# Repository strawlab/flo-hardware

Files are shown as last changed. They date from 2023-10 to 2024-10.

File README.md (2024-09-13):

# Fast-Lock-On (FLO) hardware



**ℹ️ The main FLO repository is at https://github.com/strawlab/flo ℹ️**.

This repository hosts build instructions and manual for the FLO Bring Your Own
(BYO) camera insect tracking/filming. Included are hardware design files and other large,
binary files.

FLO is a method for videography using a camera system that automatically moves
to follow the subject.

FLO is described in the following publication:

[FLO paper]: https://doi.org/10.1101/2023.12.20.572558

Vo-Doan TT, Titov VV, Harrap MJM, Lochner S, Straw AD. High Resolution Outdoor Videography of Insects Using Fast Lock-On Tracking. bioRxiv (2023) [doi:10.1101/2023.12.20.572558][FLO paper].

flo video rollup

## What is in this repository

### Mini-FLO

A bare-minimum hardware

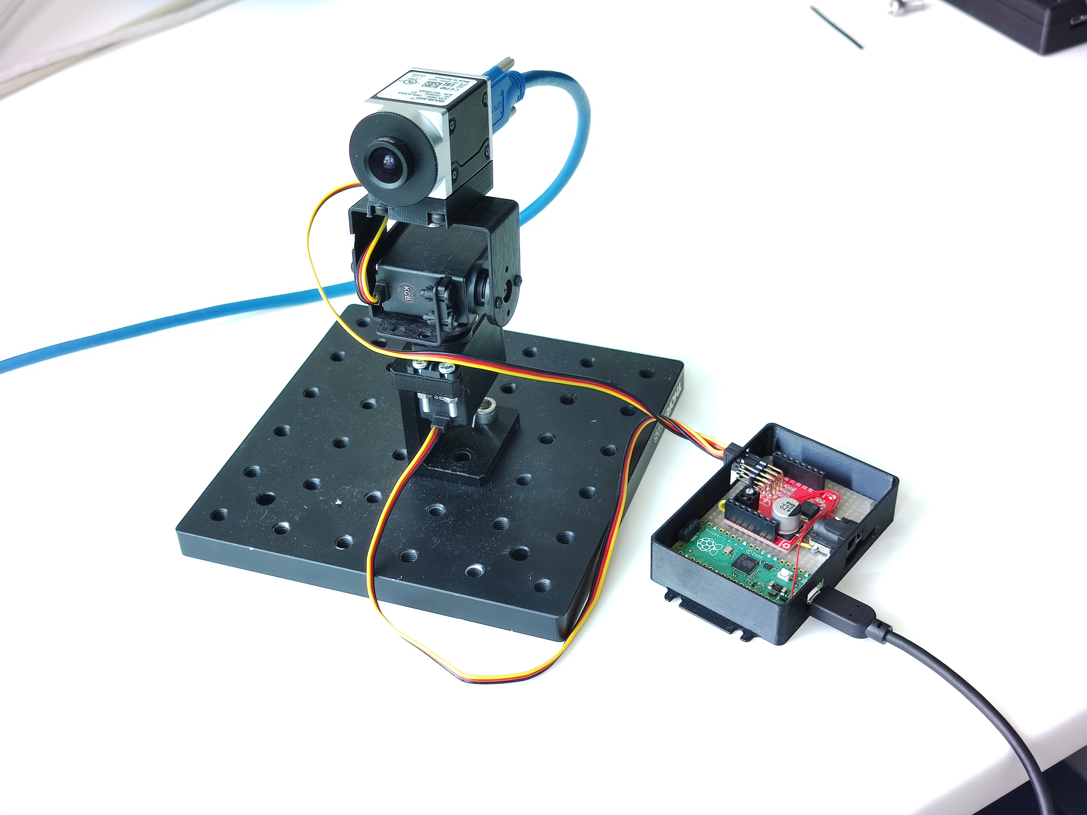
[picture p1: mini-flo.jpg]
Mini-FLO photo


### BYO-camera setup

"Bring Your Own Camera".

The setup for filming flying bees carrying a retroreflective marker.

[hardware description is in ./byo directory](./byo/readme.md)

BYO-camera setup photo

## Other links

- https://github.com/strawlab/red-button-trigger-timestamp hardware to record
  times of external trigger events.

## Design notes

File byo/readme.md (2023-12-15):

# Bill of materials

see [bom.xlsx](./bom.xlsx)

PCB files are made in KiCAD 7.0.

Some 3d-printing models were done in FreeCAD 0.21.0.32457 (pre-release of v0.21); Lattice2 and Part-o-magic community add-ons are required for editing the FreeCAD models. 

Other 3d-printing models were done in Autodesk Inventor.

The 3d models of parts are also provided in STEP and STL formats; gcode files are sliced for Prusa i3 MK3 3d printer with 0.4mm nozzle.

# System description

## overall design

## tracking cameras and illumination system

The `beam-driver` board sends trigger pulses to the two tracking cameras. The cameras send back an ExposureActive signal, which are ORed together, passed through the microcontroller (to limit the max pulse width to protect the leds and the driver from misconfiguration of exposure times) to drive the 850 nm LED beam source. Image data is sent to the PC via usb3.

Nominal exposure time is 50 microseconds, the default framerate is 150 Hz.

### beam-driver board

### beam source

These rings were designed for a different setup, and don't quite fit on the cameras of the BYO setup because they are too close to each other. So we've cut these boards, and also left some LEDs unpopulated. There is a pcb layout for the cut-down version, see `/led-ring-v2/led-ring-v2-cut`. The photo below shows the manually-cut variant of the full ring.

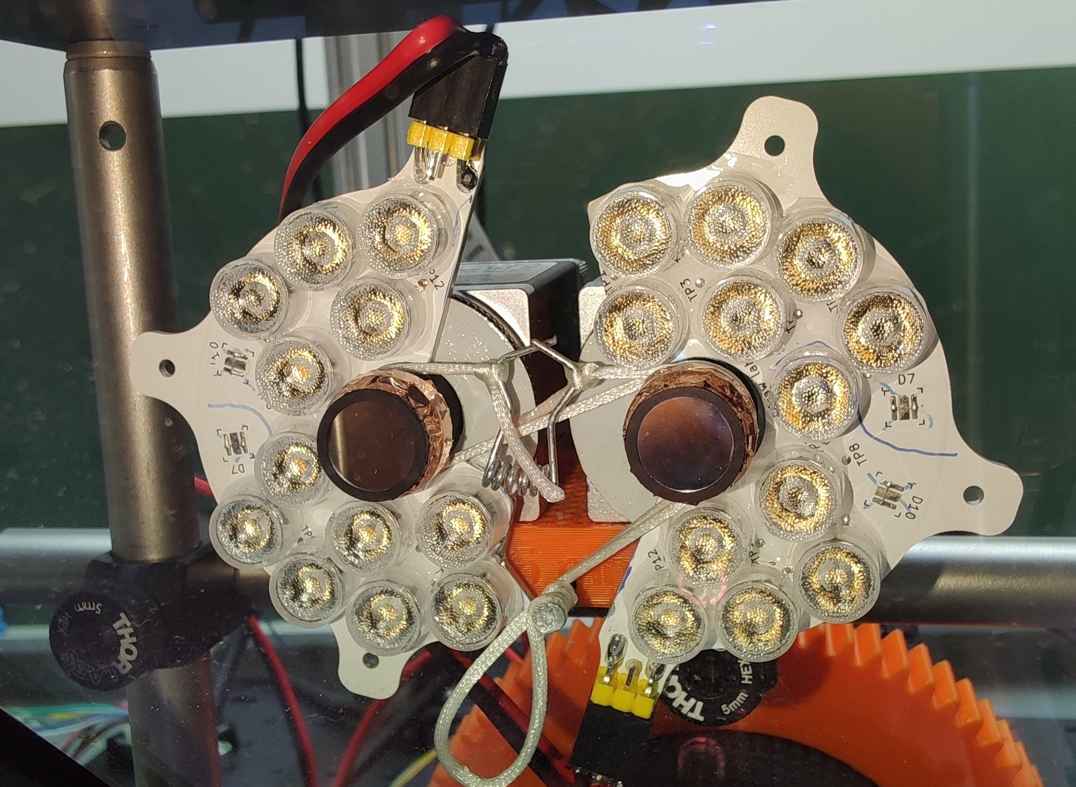
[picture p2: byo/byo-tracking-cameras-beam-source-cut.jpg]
cut beam source on byo system


### trigger cable

see [trigger cable assembly instruction](../trigger-cable/trigger-cable.md)

### tuning led current

Supply voltage directly affects the peak current of the beam source LEDs. The range allowed by the board itself is 9 to 35 V, but the actual range must be determined experimentally for each LED source. 

For our beam source (2 boards of 6-series-2-parallel SFH4715AS LEDs), the maximum supply voltage is 24 V.

1) determine the maximum current for your beam source. For example, our board uses SFH4715AS, which has a peak current rating of 3 A. We have a total of 4 string in parallel (2 strings per led board and 2 led boards), so the total current to be seen by the driver is 4 * 3 = 12 A.

2) connect one camera to the beam-driver board. Configure it for 50 us exposure. (signal generator can be used instead of a camera)

3) power the board from an adjustable power supply set to 9 V, and verify (with an oscilloscope) that you see 50-microsecond-wide pulses on the gate of the mosfet.

4) connect an oscilloscope to the SMA connector on the board with a coax cable, and set the probe division ratio to 20x (because the sense resistor is 0.05 Ohms), and the unit to Amps. (do not use 50-ohm termination on the scope).

5) crank up the supply voltage until the current pulse amplitude reaches the wanted value (12 A). Write down the voltage.

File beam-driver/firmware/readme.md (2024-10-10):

# Firmware binary

This file can be flashed onto the Raspberry Pi Pico onboard the Dual Cam PCB.
Hold the boot button while plugging in the Raspberry Pi Pico to your PC. This
will bring it up as a USB Mass Storage device onto which you can drag and drop
the `.uf2` file here.

### beamdriver-150Hz.uf2

Source code: [repo "flo", commit c64758fc95ba7cb73e0c1d8a02bef2db8ca351d4 "Merge branch 'firmware-beamdriver'"](https://github.com/strawlab/flo/tree/c64758fc95ba7cb73e0c1d8a02bef2db8ca351d4/firmware/beamdriver)

Characteristics:

- 150 fps
- lowest latency and jitter (~0.5us)
- no helpful led indication

### beamdriver-100Hz.uf2

Same source as above, compiled with `FRAMERATE` set to 100.0.

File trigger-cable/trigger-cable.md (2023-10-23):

# Trigger cable

The trigger cable connects `led-driver` board to a tracking camera. 
Two cables are needed for two cameras.

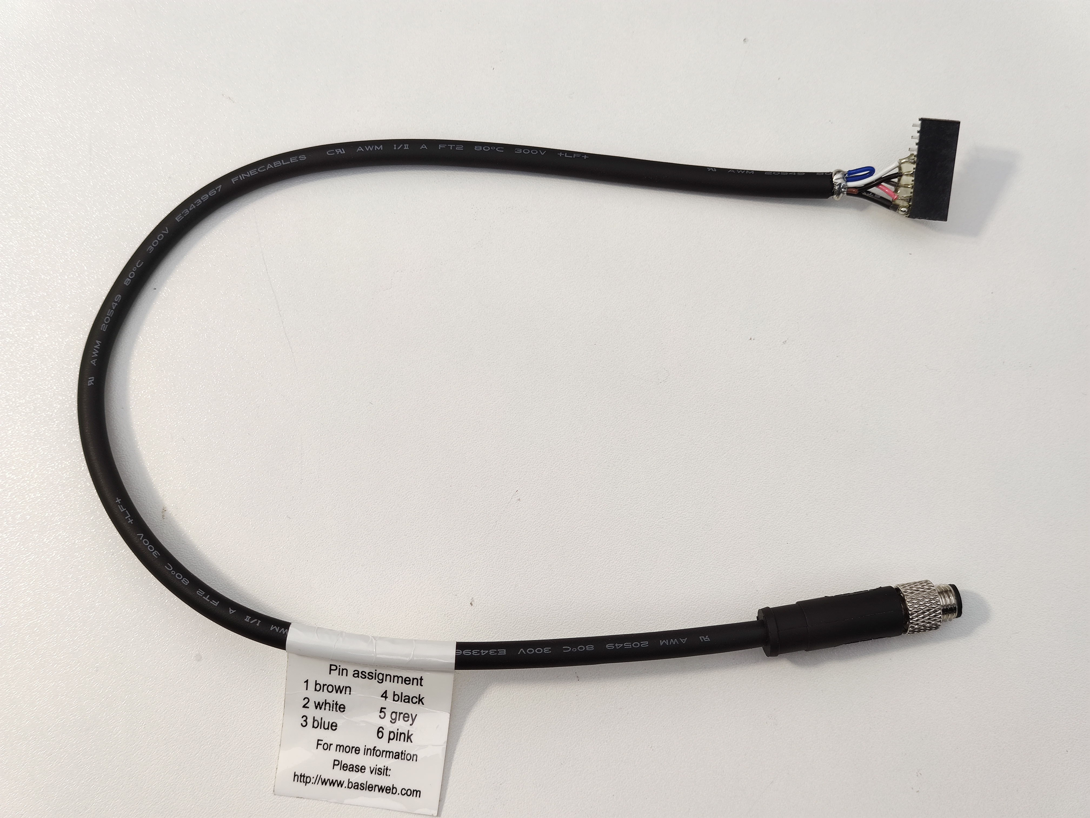
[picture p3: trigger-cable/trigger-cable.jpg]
trigger cable photo




## BOM

* Basler 2200000315
* 8x1-pin 0.1-inch socket

## Pinout

| camera connector pin  | wire color | signal        | pcb connector pin |
|-----------------------|------------|----------     |-------------------|
| 1 (nc)                | brown      | none          | none              |
| 2 (Line1)             | white      | not used      | 4                 | 
| 3 (Line1 return)      | blue       | ground        | 7, 8              | 
| 4 (Line2)             | black      | <-- trigger   | 5                 | 
| 5 (Line3)             | grey       | exposure -->  | 6                 | 
| 6 (gpio ground)       | pink       | ground        | 7, 8              | 
| shield (camera case)  |            | ground        | 7, 8              | 
|                       |            | (connector key) | 1 (plug / missing pin)              |

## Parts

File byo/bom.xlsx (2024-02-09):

no | system | type | component | brand | part number | count | detail | link | 3d model | pcb project | name on pcb
 | byo | device | high-speed camera | Mikrotron | MotionBlitz EoSens mini1 | 1
 | byo | mechanical | lens mount adapter |  | ?? | 1 | C mount to Fmount adapter
 | byo | mechanical | mounting base | Thorlabs | BA1S/M | 1 | pretty camera mount
 | byo | mechanical | cap screw 1/4''-20 3/8'' |  |  | 1 | mount ball head to post
 | byo | mechanical | ball head | Giottos | MH1004 | 1 | pretty camera mount
 | byo | optics | lens for high-speed camera | Nikon | AF Micro Nikkor 200mm f/4D | 1
 | byo/focusing | 3d-print | pinion gear |  |  | 1 | mounted onto the focusing stepper |  | byo/focusing/36jx30k5.18-pinion.FCStd
 | byo/focusing | 3d-print | motor mount |  |  | 1 |  |  | byo/focusing/36jx30k5.18-mount.FCStd
 | byo/focusing | 3d-print | ring gear |  |  | 1 | press-fit onto the barrel of the lens |  | byo/focusing/ring_gear.stl
 | byo/focusing | device | stepper driver | Trinamic | TMCM-1141 | 1
 | byo/focusing | device | power supply |  |  | 1 | 24V 1.25A
 | byo/focusing | mechanical | 1/4"-20 cap srew |  |  | 1 | fix motor mount to the lens
 | byo/focusing | mechanical | geared stepper motor | Phidgets | Phidgets id:3345_0 | 1 | NEMA17 1.8 Degree 1.68A Stepper -> 5.18:1 Gearbox, 18 kg*cm torque
 | byo/focusing | cable | USB cable |  |  | 1 | A to micro-B 3 meters, connect stepper driver to pc
 | setup | 3d-print | bottom mirror frame |  |  | 1 |  |  | byo/PanTilt/hot_mirror_holder.stl
 | setup | 3d-print | hot mirror frame |  |  | 1 |  |  | byo/PanTilt/hot_mirror_holder.stl
 | setup | laser cut | front cover |  |  | 1 |  |  | tba
 | setup | laser cut | left cover |  |  | 1 |  |  | tba
 | setup | laser cut | right corner cover |  |  | 1 |  |  | tba
 | setup | laser cut | right cover |  |  | 1 | do not cut through |  | tba
 | setup | laser cut | top right cover front |  |  | 1 |  |  | tba
 | setup | laser cut | top right cover back |  |  | 1 |  |  | tba
 | setup | laser cut | top cover |  |  | 1 |  |  | tba
 | setup | mechanical | M6x8 mm setscrew |  |  | 8 | mount all the posts to base plate
 | setup | mechanical | M4x8 mm cap screw |  |  | 4 | mount the pantilt head to the posts
 | setup | mechanical | base plate | Thorlabs | MB3060 | 1 | Aluminum Breadboard, 300 mm x 600 mm x 12.7 mm, M6 Taps
 | setup | mechanical | optical post | Thorlabs | TR250/M | 4 | 250mm D12.7
 | setup | mechanical | optical post | Thorlabs | TR200/M | 1 | 200mm D12.7
 | setup | mechanical | optical post | Thorlabs | TR150/M | 2 | 150mm D12.7
 | setup | mechanical | optical post | Thorlabs | TR20/M | 1 | 20mm D12.7
 | setup | mechanical | optical post | Thorlabs | TR30/M | 1 | 30mm D12.7
 | setup | mechanical | right-angle clamp | Thorlabs | RA90/M | 3
 | setup | mechanical | pedestal post holder | Thorlabs | BE1/M | 1
 | setup | mechanical | clamping fork | Thorlabs | CF125 | 1
 | setup | optics | bottom mirror |  |  | 1 | 1-st surface mirror, 101*127mm, 3mm thickness
 | setup | optics | hot mirror | Edmund | #64-462 | 1 | high performance hot mirror (101x127mm) that only reflects IR
 | tracking/beam | pcb | beam source |  | led-ring-v2-cut | 2 | reduced version of led-ring-v2 for byo |  |  | led-ring-v2/led-ring-v2-cut/led-ring-v2-cut.kicad_pro
 | tracking/beam/led-ring-v2-cut | 3d-print | lens carrier |  | lens holder v3 | 0 | carrier for aligning lenses onto LEDs. Only needed for assembly, not included in the final build. |  | led-ring-v2/lens holder v3.FCStd
 | tracking/beam/led-ring-v2-cut | electronic component | LED | Osram | SFH4715AS | 24 | 850 nm 2-stacked-junction high-power LED
 | tracking/beam/led-ring-v2-cut | electronic component | connector |  |  | 2 | 0.1-inch 2x6 pin header, straight
 | tracking/beam/led-ring-v2-cut | optics | lens for LED | Ledil | C17522_LISA4-M | 24 | 24-deg collimating reflector. Mounted by glueing.
 | tracking/led-driver | cable | power cable |  |  | 1 | banana to XT-30
 | tracking/led-driver | cable | led cable |  |  | 2 | approx 400 mm length 2-conductor 0.5 mm2
 | tracking/led-driver | device | adjustable power supply | Manson | HCS-3202 | 1 | adjustable power supply for led driver. Nominal 24 V 1 A. Adjusting the voltage changes led current.
 | tracking/led-driver | pcb | led driver/camera sync |  |  | 1 |  |  |  | beam-driver/dual-cam-pcb v2/dual-cam-pcb.kicad_pro
 | tracking/led-driver/dual-cam-pcb-v2 | electronic component | SMA connector through-hole | LPRS | 471-SMACONNECTOR | 1 |  |  |  | beam-driver/dual-cam-pcb v2/dual-cam-pcb.kicad_pro | J3
 | tracking/led-driver/dual-cam-pcb-v2 | electronic component | 0.1-inch socket (through-hole) 2x3 |  |  | 2 | there is a missing hole on the board as a polarity key. Plug the hole in the socket, and remove the corresponding pin from the plug. |  |  | beam-driver/dual-cam-pcb v2/dual-cam-pcb.kicad_pro | J4,J5
 | tracking/led-driver/dual-cam-pcb-v2 | electronic component | 0.1-inch pin header straight 1x3 |  |  | 2 | optional (intended for connecting pan-tilt hobby servo motors) |  |  | beam-driver/dual-cam-pcb v2/dual-cam-pcb.kicad_pro | J6, J7
 | tracking/led-driver/dual-cam-pcb-v2 | electronic component | XT-30 connector | Amass | XT30U-M | 1 |  |  |  | beam-driver/dual-cam-pcb v2/dual-cam-pcb.kicad_pro | J8
 | tracking/led-driver/dual-cam-pcb-v2 | electronic component | n-channel MOSFET | Toshiba | TK6R7P06PL | 1 |  |  |  | beam-driver/dual-cam-pcb v2/dual-cam-pcb.kicad_pro | Q1
 | tracking/led-driver/dual-cam-pcb-v2 | electronic component | resistor 20 KOhm, size 0605 |  |  | 1 |  |  |  | beam-driver/dual-cam-pcb v2/dual-cam-pcb.kicad_pro | R1
 | tracking/led-driver/dual-cam-pcb-v2 | electronic component | resistor 510 ohm, size 0605 |  |  | 1 |  |  |  | beam-driver/dual-cam-pcb v2/dual-cam-pcb.kicad_pro | R10
 | tracking/led-driver/dual-cam-pcb-v2 | electronic component | resistor 10 ohms, size 0605 |  |  | 1 |  |  |  | beam-driver/dual-cam-pcb v2/dual-cam-pcb.kicad_pro | R11
 | tracking/led-driver/dual-cam-pcb-v2 | electronic component | resistor 0.05 ohm, size 2010 | Ohmite | LVK12R050DER | 1 |  |  |  | beam-driver/dual-cam-pcb v2/dual-cam-pcb.kicad_pro | R12
 | tracking/led-driver/dual-cam-pcb-v2 | electronic component | 1 Ohm 1 W through-hole resistor | SEI Stackpole | RSMF2JT1R00 | 4 |  |  |  | beam-driver/dual-cam-pcb v2/dual-cam-pcb.kicad_pro | R14,R16,R15,R17
 | tracking/led-driver/dual-cam-pcb-v2 | electronic component | MLCC 10uF 16V, size 0805 |  |  | 1 | bypass cap, value is not critical |  |  | beam-driver/dual-cam-pcb v2/dual-cam-pcb.kicad_pro | C1
 | tracking/led-driver/dual-cam-pcb-v2 | electronic component | resistor 51 ohms, size 0605 | Yageo | RT0603DRE0751RL | 9 |  |  |  | beam-driver/dual-cam-pcb v2/dual-cam-pcb.kicad_pro | R19,R6,R2,R3,R8,R13,R5,R18,R4
 | tracking/led-driver/dual-cam-pcb-v2 | electronic component | resistor 1 KOhm, size 0605 |  |  | 2 |  |  |  | beam-driver/dual-cam-pcb v2/dual-cam-pcb.kicad_pro | R20,R21
 | tracking/led-driver/dual-cam-pcb-v2 | electronic component | resistor 10 KOhm, size 0605 |  |  | 1 |  |  |  | beam-driver/dual-cam-pcb v2/dual-cam-pcb.kicad_pro | R7
 | tracking/led-driver/dual-cam-pcb-v2 | electronic component | resistor 4.3 KOhm, size 0605 |  |  | 1 |  |  |  | beam-driver/dual-cam-pcb v2/dual-cam-pcb.kicad_pro | R9
 | tracking/led-driver/dual-cam-pcb-v2 | electronic component | Raspberry-Pi Pico | Raspberry-Pi | Raspberry-Pi Pico | 1 |  |  |  | beam-driver/dual-cam-pcb v2/dual-cam-pcb.kicad_pro | U1
 | tracking/led-driver/dual-cam-pcb-v2 | electronic component | gate driver UCC27624DR | Texas Instruments | UCC27624DR | 1 |  |  |  | beam-driver/dual-cam-pcb v2/dual-cam-pcb.kicad_pro | U2
 | tracking/led-driver/dual-cam-pcb-v2 | electronic component | LM317L (SOT-89) | Texas Instruments | LM317LIPK | 1 |  |  |  | beam-driver/dual-cam-pcb v2/dual-cam-pcb.kicad_pro | U3
 | tracking/led-driver/dual-cam-pcb-v2 | electronic component | 7805 (TO220) | JRC | NJM7805FA | 1 |  |  |  | beam-driver/dual-cam-pcb v2/dual-cam-pcb.kicad_pro | U4
 | tracking/led-driver/dual-cam-pcb-v2 | electronic component | MLCC 1uF 35V, size 0805 |  |  | 1 | bypass cap, value is not critical |  |  | beam-driver/dual-cam-pcb v2/dual-cam-pcb.kicad_pro | C2
 | tracking/led-driver/dual-cam-pcb-v2 | electronic component | Electrolytic capacitor 3300uF 35V |  |  | 1 | overkill. 1200uF should be enough. |  |  | beam-driver/dual-cam-pcb v2/dual-cam-pcb.kicad_pro | C3
 | tracking/led-driver/dual-cam-pcb-v2 | electronic component | MLCC 22uF 6.5V, size 0805 | Kyocera | CM105X5R226M16AT | 1 | affects stability of 7805, value is important |  |  | beam-driver/dual-cam-pcb v2/dual-cam-pcb.kicad_pro | C7
 | tracking/led-driver/dual-cam-pcb-v2 | electronic component | MLCC 200pF 6.5V, size 0603 |  |  | 2 | emi filter, value is important |  |  | beam-driver/dual-cam-pcb v2/dual-cam-pcb.kicad_pro | C8,C9
 | tracking/led-driver/dual-cam-pcb-v2 | electronic component | schottky diode (Micro-MELF) | Vishay | BAS85-GS08 | 2 |  |  |  | beam-driver/dual-cam-pcb v2/dual-cam-pcb.kicad_pro | D2,D1
 | tracking/led-driver/dual-cam-pcb-v2 | electronic component | schottky diode size 0805 | Kyocera | SD0805S020S1R0 | 3 |  |  |  | beam-driver/dual-cam-pcb v2/dual-cam-pcb.kicad_pro | D4,D5,D3
 | tracking/led-driver/dual-cam-pcb-v2 | electronic component | 0.1 inch pin header straight 1x8 |  |  | 2 |  |  |  | beam-driver/dual-cam-pcb v2/dual-cam-pcb.kicad_pro | J2,J1
 | tracking/led-driver/led-cable | electronic component | led-side connector |  |  | 2 | 2x6 0.1-inch socket
 | tracking/led-driver/led-cable | electronic component | driver-side connector |  |  | 2 | 2x6 0.1-inch pin header
 | tracking/led-driver/led-cable | electronic component | ferrite bead | Kemet | ESD-R-10E | 2
 | tracking/led-driver/power-cable | electronic component | power connector | Amass | XT30U | 1
 | tracking/pantilt | 3d-print | Pan motor pulley |  |  | 1 |  |  | byo/PanTilt/Pan_Pulley_17.stl
 | tracking/pantilt | 3d-print | Pan motor plate |  |  | 1 |  |  | byo/PanTilt/Pan_motor_plate.stl
 | tracking/pantilt | 3d-print | Pan motor stopper |  |  | 1 |  |  | byo/PanTilt/Pan_motor_stop.stl
 | tracking/pantilt | 3d-print | Pan rotor |  |  | 1 |  |  | byo/PanTilt/Pan_Rotor_245.stl
 | tracking/pantilt | 3d-print | Pan base |  |  | 1 |  |  | byo/PanTilt/Pan_base.stl
 | tracking/pantilt | 3d-print | Pan bearing stopper bottom |  |  | 1 |  |  | byo/PanTilt/Pan_bearing_stop_bottom.stl
 | tracking/pantilt | 3d-print | Pan bearing stopper top |  |  | 1 |  |  | byo/PanTilt/Pan_bearing_stop_top.stl
 | tracking/pantilt | 3d-print | Tilt base |  |  | 1 |  |  | byo/PanTilt/Tilt_base.stl
 | tracking/pantilt | 3d-print | Tilt motor base |  |  | 1 |  |  | byo/PanTilt/Tilt_base_motor_side.stl
 | tracking/pantilt | 3d-print | Tilt motor pulley |  |  | 1 |  |  | byo/PanTilt/Tilt_Motor_pulley_20.stl
 | tracking/pantilt | 3d-print | Tilt motor spacer |  |  | 1 |  |  | byo/PanTilt/Tilt_motor_spacer.stl
 | tracking/pantilt | 3d-print | Tilt bearing stopper |  |  | 2 |  |  | byo/PanTilt/Tilt_bearing_stop.stl
 | tracking/pantilt | 3d-print | Pantilt head cover |  |  | 1 |  |  | byo/PanTilt/Pan_cover.stl
 | tracking/pantilt | 3d-print | Pan tensioner knot |  |  | 1 |  |  | byo/PanTilt/Pan_tension_knot.stl
 | tracking/pantilt | 3d-print | Tilt bearing |  | 61802-2RS | 2 | ball bearing 61802-2RS
 | tracking/pantilt | 3d-print | Tilt rotor |  |  | 1 |  |  | byo/PanTilt/Tilt_mirror_rotor.stl
 | tracking/pantilt | 3d-print | Tilt rotor pulley |  |  | 1 |  |  | byo/PanTilt/Tilt_Rotor_pulley_100.stl
 | tracking/pantilt | 3d-print | moving mirror assembly |  |  | 1 |  |  | ??
 | tracking/pantilt | cable | USB cable |  |  | 2 | A to micro-B 3 meters, connect steppers to pc
 | tracking/pantilt | device | smart stepper | Trinamic | PD42-2-1240-TMCL | 2
 | tracking/pantilt | device | power supply |  |  | 2 | 12V 2A power supply for smart stepper
 | tracking/pantilt | electronic component | wires for smart stepper | Trinamic | TMCM-110-CABLE | 2 | 4-pin JST-PH connector with wires, for powering steppers
 | tracking/pantilt | mechanical | M5x30 cap srew |  |  | 1 | press fit to the pan tension knot and use for adjusting pan belt tesion
 | tracking/pantilt | mechanical | M3x8 cap srew |  |  | 8 | mount pan motor to pan motor plate and the tilt bases to pan rotor
 | tracking/pantilt | mechanical | M3x12 cap screw |  |  | 4 | mount tilt motor to tilt motor base
 | tracking/pantilt | mechanical | M1.5x5 cap srew |  |  | 8 | fixed pan bearing stoper top to pan base
 | tracking/pantilt | mechanical | M5 female insert |  |  | 1 | heat by soldering iron and insert to the pan motor plate
 | tracking/pantilt | mechanical | M3 female insert |  |  | 4 | heat by soldering iron and insert to the pan rotor
 | tracking/pantilt | mechanical | belt (pan) |  | 256MXL | 1 | GT2 profile 256 teeth 6.5mm width
 | tracking/pantilt | mechanical | belt (tilt) |  | 880MXL | 1 | GT2 profile 110 teeth 5mm width
 | tracking/pantilt | optics | mirror |  |  | 1 | 1-st surface mirror, 140*140mm square with 16mm chamfer on corners, thickness 3mm
 | tracking/pantilt/panbearing | 3d-print | Pan bearing inner cage |  |  | 1 |  |  | byo/PanTilt/Pan_bearing_inner.stl
 | tracking/pantilt/panbearing | 3d-print | Pan bearing middle ring |  |  | 1 |  |  | byo/PanTilt/Pan_bearing_middle.stl
 | tracking/pantilt/panbearing | 3d-print | Pan bearing outer cage |  |  | 1 |  |  | byo/PanTilt/Pan_bearing_outter.stl
 | tracking/pantilt/panbearing | mechanical | Pan bearing balls (4.5 mm) |  |  | 12 | 4.5 mm stainless steal ball insert to the pan bearing
 | tracking/sensor | 3d-print | camera mount |  |  | 1 |  |  | byo/2cam-plate-35mm/2cam-plate-35mm.FCStd
 | tracking/sensor/camera | cable | USB cable |  |  | 2 | USB3 cable for connecting the camera to the PC
 | tracking/sensor/camera | cable | trigger cable | Basler | 2200000315 | 2
 | tracking/sensor/camera | device | tracking camera | Basler | a2A 1920 - 160umBAS | 2 | monochrome, ir-sensitive camera. The front of the case must be machined to make it CS-mount.
 | tracking/sensor/camera | mechanical | CS to S-mount lens adapter | Basler | 2000035953 | 2
 | tracking/sensor/camera | optics | lens | IDS-imaging | IDS-5M12-S2524F | 2 | 25-mm, 1/2in sensor, S-mount (has ir-blocking filter which must be removed)
 | tracking/sensor/camera | optics | IR bandpass filter | Thorlabs | FBH05850-10 | 2 | 850 nm, fwhm=10 nm
 |  |  | PC |  |  | 1 | amd ryzen 9 3900x, 32G ram, nvidia rtx3060ti

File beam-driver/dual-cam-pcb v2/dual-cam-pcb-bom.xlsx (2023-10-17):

Id | Designator | Footprint | Quantity | Designation | Supplier and ref | brand | comment
23 | C1 | C_0805_2012Metric_Pad1.18x1.45mm_HandSolder | 1 | MLCC 10uF 16V, size 0805 |  |  | bypass cap, value is not critical
26 | C2 | C_0805_2012Metric_Pad1.18x1.45mm_HandSolder | 1 | MLCC 1uF 35V, size 0805 |  |  | bypass cap, value is not critical
8 | C3 | CP_Radial_D18.0mm_P7.50mm | 1 | Electrolytic capacitor 3300uF 35V |  |  | overkill. 1200uF should be enough.
17 | C7 | C_0805_2012Metric_Pad1.18x1.45mm_HandSolder | 1 | MLCC 22uF 6.5V, size 0805 |  |  | affects stability of 7805, value is important
25 | C8,C9 | C_0603_1608Metric_Pad1.08x0.95mm_HandSolder | 2 | MLCC 200pF 6.5V, size 0603 |  |  | emi filter, value is important
21 | D2,D1 | D_MicroMELF_Handsoldering | 2 | schottky diode (Micro-MELF) | BAS85-GS08 | Vishay
12 | D4,D5,D3 | D_0805_2012Metric_Pad1.15x1.40mm_HandSolder | 3 | schottky diode size 0805 | SD0805S020S1R0 | Kyocera
3 | J2,J1 | PinHeader_1x08_P2.54mm_Vertical | 2 | 0.1 inch pin header straight 1x8
2 | J3 | SMA_Amphenol_901-144_Vertical | 1 | SMA connector through-hole | 471-SMACONNECTOR | LPRS
4 | J4,J5 | Conn_LED_source | 2 | 0.1-inch socket (through-hole) 2x3 |  |  | there is a missing hole on the board as a polarity key. Plug the hole in the socket, and remove the corresponding pin from the plug.
9 | J6, J7 | PinHeader_1x03_P2.54mm_Vertical | 2 | 0.1-inch pin header straight 1x3 |  |  | optional (intended for connecting pan-tilt hobby servo motors)
7 | J8 | AMASS_XT30U-M_1x02_P5.0mm_Vertical | 1 | XT-30 connector | XT60U-M | Amass
22 | Q1 | TO-252-2 | 1 | n-channel MOSFET | TK6R7P06PL | Toshiba
24 | R1 | R_0603_1608Metric_Pad0.98x0.95mm_HandSolder | 1 | resistor 20 KOhm, size 0605
19 | R10 | R_0603_1608Metric_Pad0.98x0.95mm_HandSolder | 1 | resistor 510 ohm, size 0605
11 | R11 | R_0603_1608Metric_Pad0.98x0.95mm_HandSolder | 1 | resistor 10 ohms, size 0605
14 | R12 | R_2010_5025Metric_Pad1.40x2.65mm_HandSolder | 1 | resistor 0.05 ohm, size 2010 | LVK12R050DER | Ohmite
1 | R14,R16,R15,R17 | R_Axial_DIN0411_L9.9mm_D3.6mm_P5.08mm_Vertical | 4 | 1 Ohm 1 W through-hole resistor
13 | R19,R6,R2,R3,R8,R13,R5,R18,R4 | R_0603_1608Metric_Pad0.98x0.95mm_HandSolder | 9 | resistor 51 ohms, size 0605
18 | R20,R21 | R_0603_1608Metric_Pad0.98x0.95mm_HandSolder | 2 | resistor 1 KOhm, size 0605
16 | R7 | R_0603_1608Metric_Pad0.98x0.95mm_HandSolder | 1 | resistor 10 KOhm, size 0605
27 | R9 | R_0603_1608Metric_Pad0.98x0.95mm_HandSolder | 1 | resistor 4.3 KOhm, size 0605
5 | U1 | RPi_Pico_SMD | 1 | Raspberry-Pi Pico | Raspberry-Pi Pico | Raspberry-Pi
20 | U2 | SOIC-8_3.9x4.9mm_P1.27mm | 1 | gate driver UCC27624DR | UCC27624DR | Texas Instruments
15 | U3 | SOT-89-3 | 1 | LM317L (SOT-89) | LM317LIPK | Texas Instruments
6 | U4 | TO-220-3_Vertical | 1 | 7805 (TO220) | NJM7805FA | JRC

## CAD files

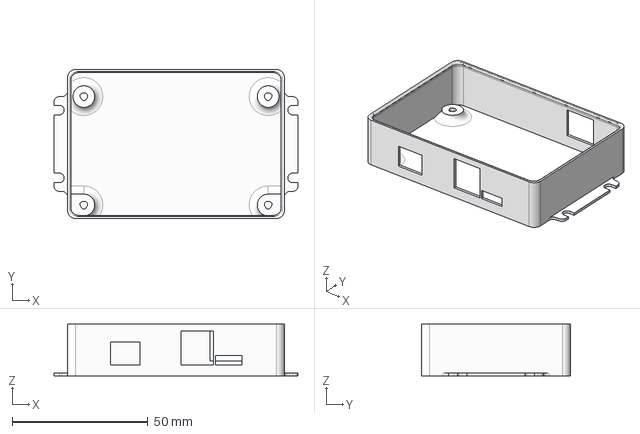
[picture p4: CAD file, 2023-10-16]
beam-driver/board outline.FCStd
90.0 x 55.0 x 19.0 mm

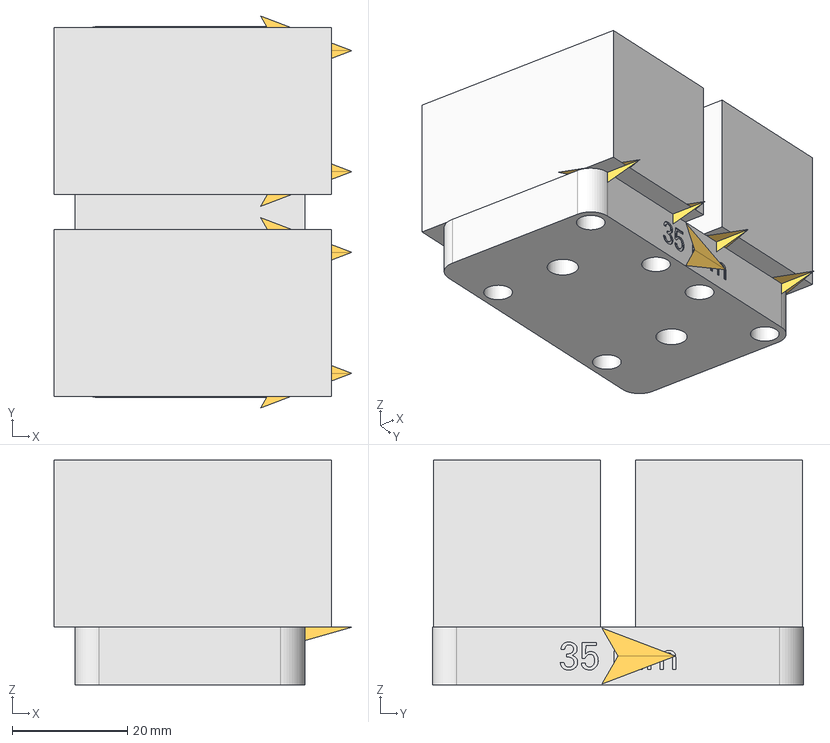
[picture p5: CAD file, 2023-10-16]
byo/2cam-plate-35mm/2cam-plate-35mm.FCStd
51.7 x 68.0 x 39.0 mm
BoundBox of ace2_a2a_ultra_simplified
BoundBox of ace2_a2a_ultra_simplified001
PlacementSubsequence
Placment002
Placment003

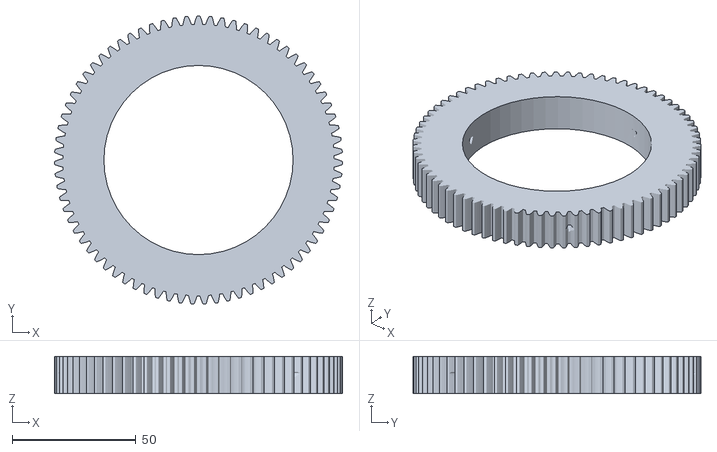
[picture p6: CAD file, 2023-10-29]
byo/focusing/ring_gear.stl
116.5 x 116.5 x 15.0

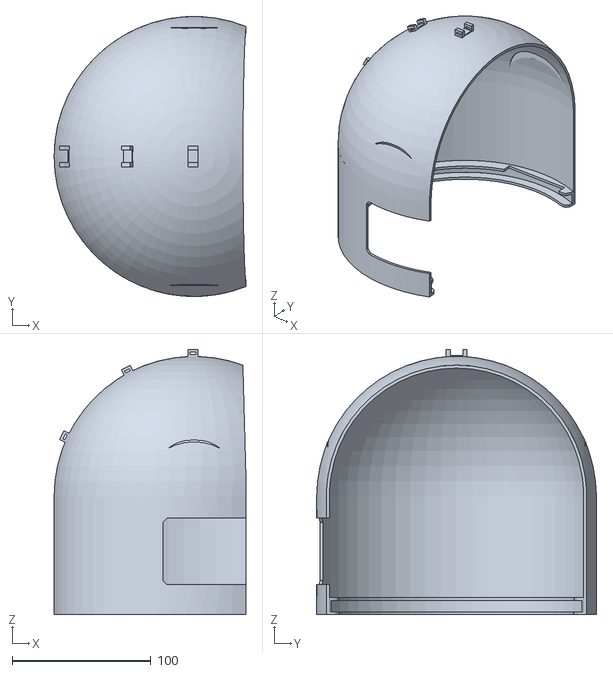
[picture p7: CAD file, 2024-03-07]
byo/PanTilt/Pan_cover_2mm.stl
138.3 x 201.9 x 191.2

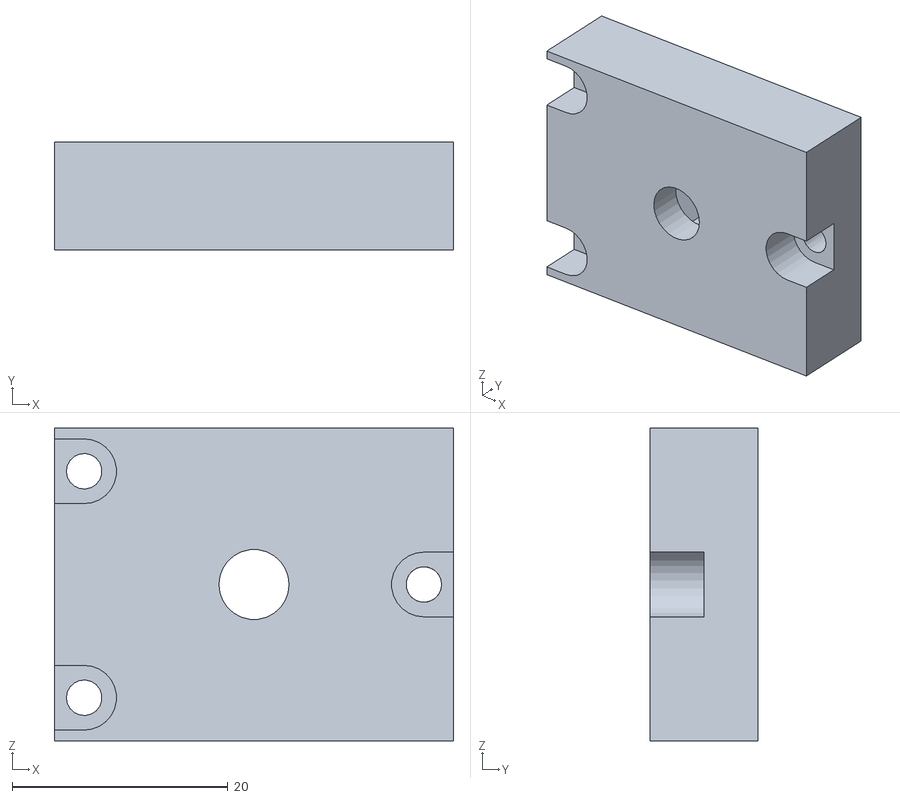
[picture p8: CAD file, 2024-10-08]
mini-pan-tilt/a2A1920_adapter_6mm.stl
37.0 x 10.0 x 29.0

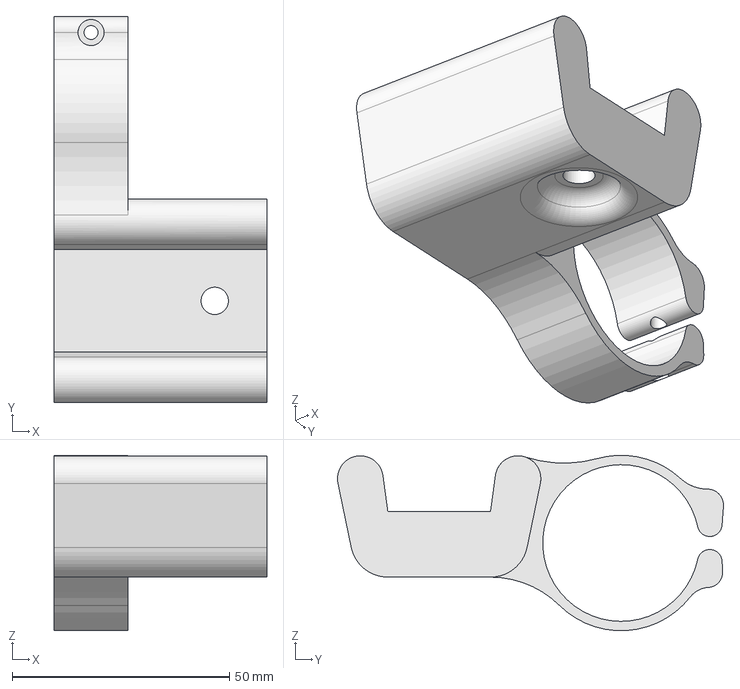
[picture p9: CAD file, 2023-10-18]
byo/focusing/36jx30k5.18-mount.step
49.0 x 88.9 x 40.4 mm

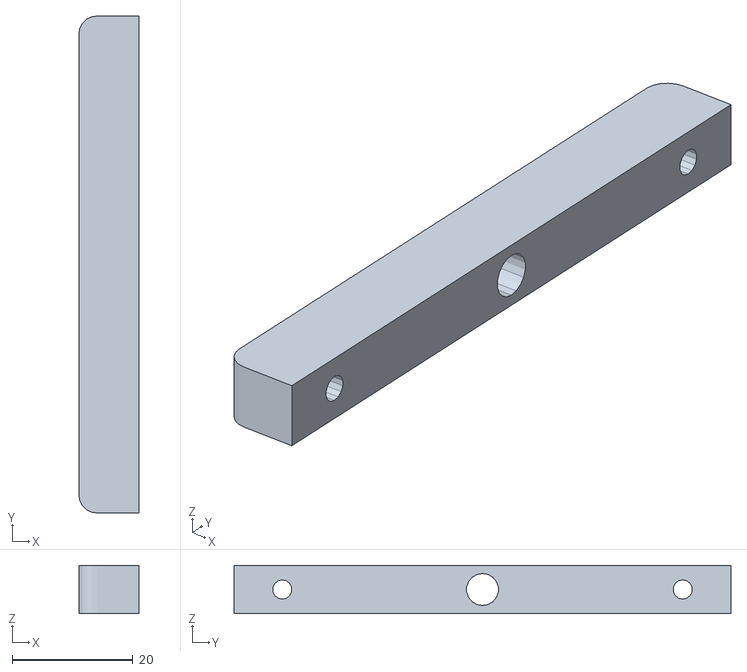
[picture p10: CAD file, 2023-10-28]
byo/PanTilt/Pan_motor_stop.stl
10.0 x 82.3 x 8.00

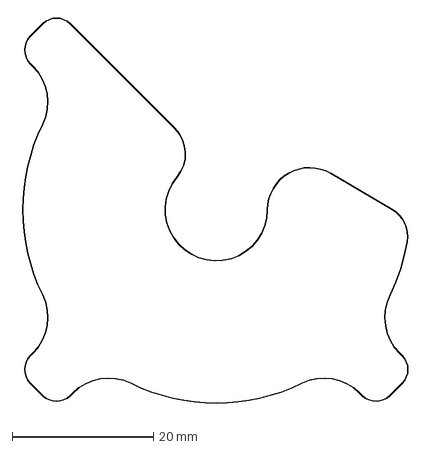
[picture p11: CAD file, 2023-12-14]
led-ring-v2/10mm lens packing (cut version)-board outline.dxf
55.8 x 55.8 mm

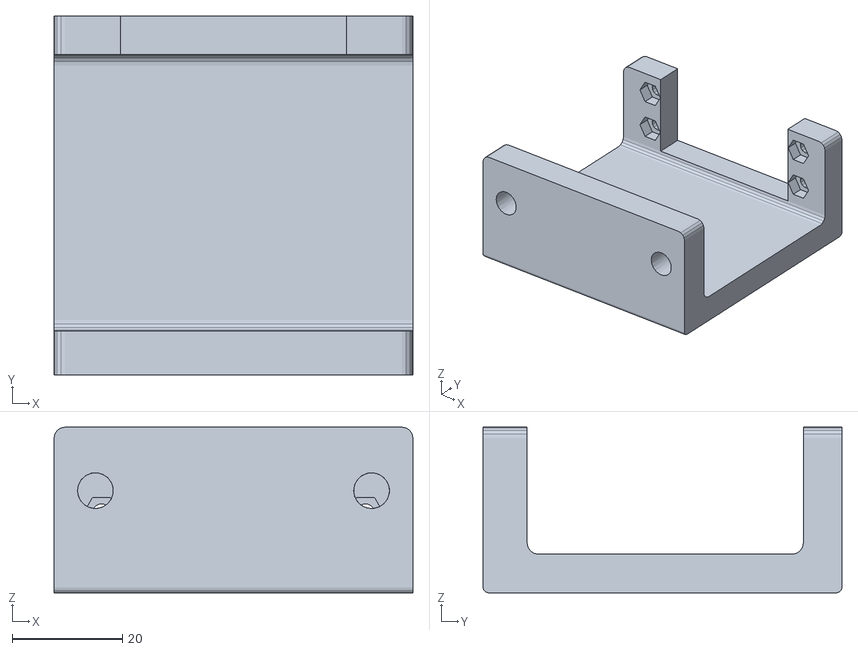
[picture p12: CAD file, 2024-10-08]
mini-pan-tilt/motor_holder.stl
65.0 x 65.0 x 30.0

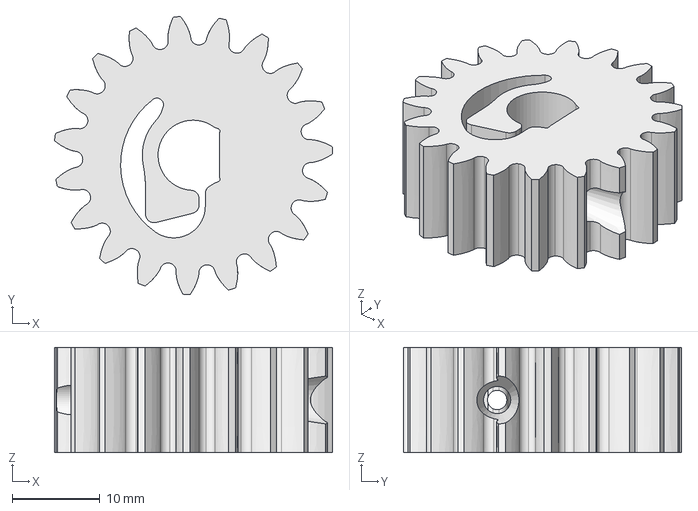
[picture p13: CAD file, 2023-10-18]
byo/focusing/36jx30k5.18-pinion.step
31.7 x 31.7 x 12.0 mm

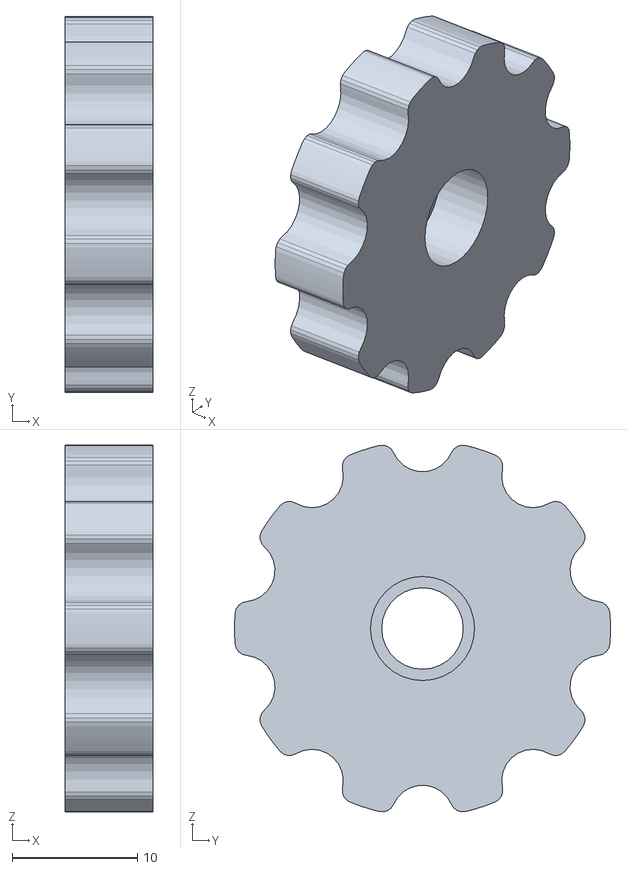
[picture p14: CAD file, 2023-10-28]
byo/PanTilt/Pan_tension_knot.stl
7.00 x 30.0 x 29.2

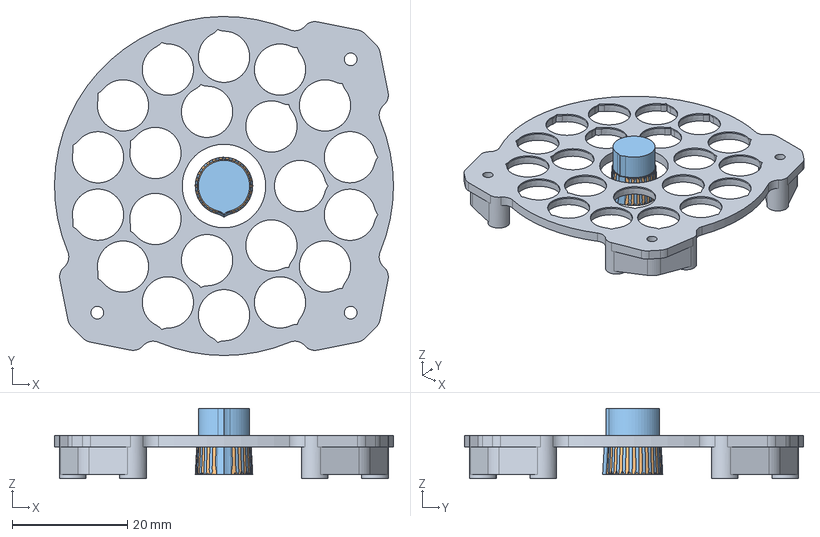
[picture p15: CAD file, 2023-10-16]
led-ring-v2/lens holder v2.FCStd
58.9 x 58.9 x 12.2 mm
lens holder
lens shape
cavity cutter

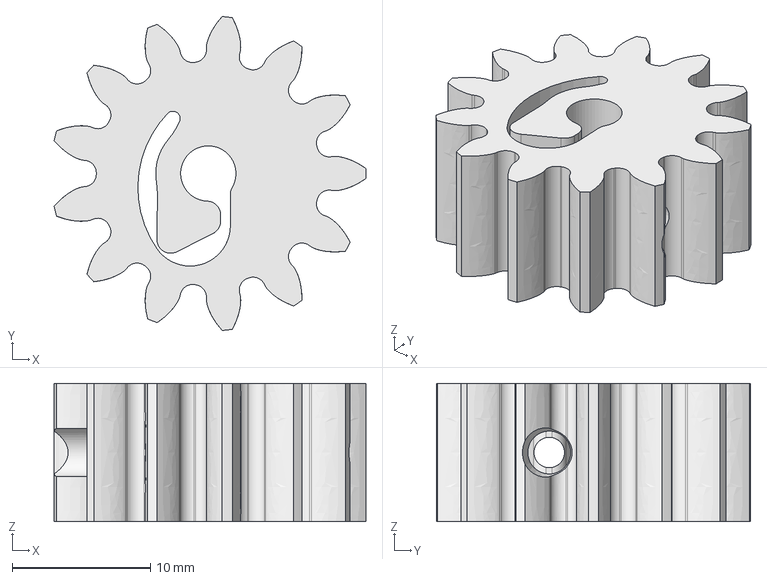
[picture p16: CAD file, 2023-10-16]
byo/focusing/nema08-pinion.FCStd
22.6 x 22.7 x 10.0 mm

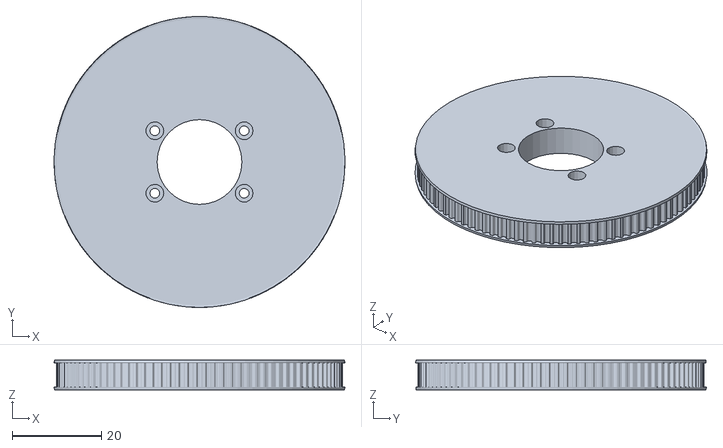
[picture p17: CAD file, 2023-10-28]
byo/PanTilt/Tilt_Rotor_pulley_100.stl
65.2 x 65.2 x 6.65

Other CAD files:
led-ring-v2/10mm lens packing (cut version).FCStd
led-ring-v2/pasting plate.FCStd
byo/PanTilt/Pan_cover.stl
led-ring-v2/10mm lens packing-Compound.dxf
byo/2cam-plate-35mm/2cam-plate-35mm.stl
byo/PanTilt/Pan_Pulley_17.stl
byo/PanTilt/Pan_Rotor_245.stl
byo/PanTilt/Pan_base.stl
byo/PanTilt/Pan_bearing_inner.stl
byo/PanTilt/Pan_bearing_middle.stl
byo/PanTilt/Pan_bearing_outter.stl
byo/PanTilt/Pan_bearing_stop_bottom.stl
byo/PanTilt/Pan_bearing_stop_top.stl
byo/PanTilt/Pan_motor_plate.stl
byo/PanTilt/Tilt_Motor_pulley_20.stl
byo/PanTilt/Tilt_base.stl
byo/PanTilt/Tilt_base_motor_side.stl
byo/PanTilt/Tilt_bearing_stop.stl
byo/PanTilt/Tilt_mirror_rotor.stl
byo/PanTilt/Tilt_motor_spacer.stl
byo/PanTilt/hot_mirror_holder.stl
byo/focusing/36jx30k5.18-mount.FCStd
byo/focusing/36jx30k5.18-mount.stl
byo/focusing/36jx30k5.18-pinion.FCStd
byo/focusing/36jx30k5.18-pinion.stl
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

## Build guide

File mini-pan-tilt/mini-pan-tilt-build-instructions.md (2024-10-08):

# Build instructions and user manual for the proof-of-concept Mini-Pan-Tilt (MPT) version of the Fast-Lock-On (FLO) insect tracking system

This manual is a step-by-step guide to assemble a mini-pan-tilt setup from
scratch and run it on an Ubuntu Linux machine.

## Bill of Materials

All parts but one, the custom 3D-printed support bracket _(CAD file included)_ are available as off-the-shelf components.

### Mechanical parts

- 1x Lynxmotion: Lynx B - Pand and Tilt Kit (Black Anodized), inluding:

  - 1x Aluminum Multi-Purpose Servo Bracket Single (ASB-04)
  - 1x Auminum "C" Servo Bracket Single (ASB-03)
  - 2x HS-422 standard servo (S422)
  - Hardware (in particular: 4x small black screws for servos, 1x black M1 screw with washer and nut for tilt axis, nylon rivets)

  There seems to be the newer version of this kit, available [here](https://www.robotshop.com/products/lynxmotion-pan-and-tilt-kit-aluminium2).

- 1x [Thorlabs base plate 150x150x12.7 mm, M6 Taps](https://www.thorlabs.de/thorproduct.cfm?partnumber=MB1515/M) +

- 1x [custom 3D printed support bracket](motor_holder.stl)

- 1x Basler Tripod Adapter, compatible with camera (see [below](#optical), e.g. [this one](https://www.edmundoptics.eu/p/ace2-14-tripod-mount-adapter/44087/)). Alternatively, there is also a 3D [printed version](a2A1920_adapter_6mm.stl) of this part.
  )
- assorted screws

  - 4x M3x20 cap screws + nuts

  - 1x M6 cap screw

  - screws required for the camera adapter

### Electronics

- [Raspberry Pi Pico](https://www.raspberrypi.com/products/raspberry-pi-pico/) microcontroller
- optional: breadboard jumper wires

### Optical

- Basler or Vimba high-framerate, USB 3.0 camera: highly recommended [Basler Ace2 a2a1920-160mBAS](https://www.baslerweb.com/en/shop/a2a1920-160umbas/)
- CS-mount lens of desired specifications. Recommended for this basic setup: f=16mm A=1:1.6
- optional: IR-bandpass filter for better signal-to-noise ratio

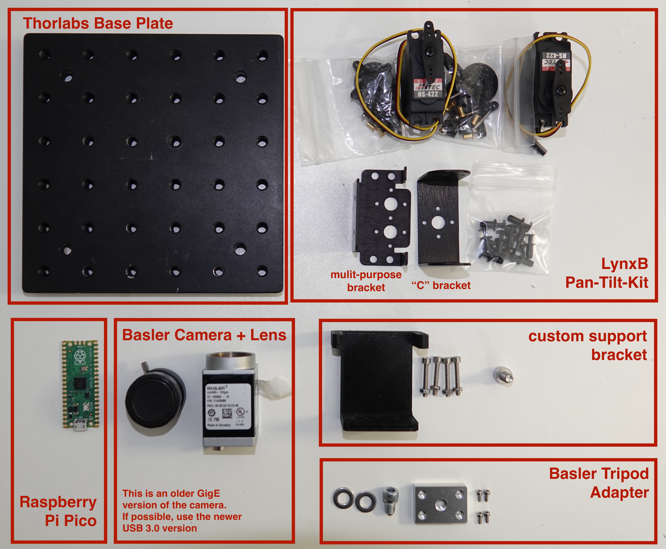
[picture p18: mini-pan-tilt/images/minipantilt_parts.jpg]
parts


## Hardware build instruction

1. Mount camera on "C" bracket :
   - Attach tripod adapter to base of camera
   - Attach "C" Bracket to Adapter

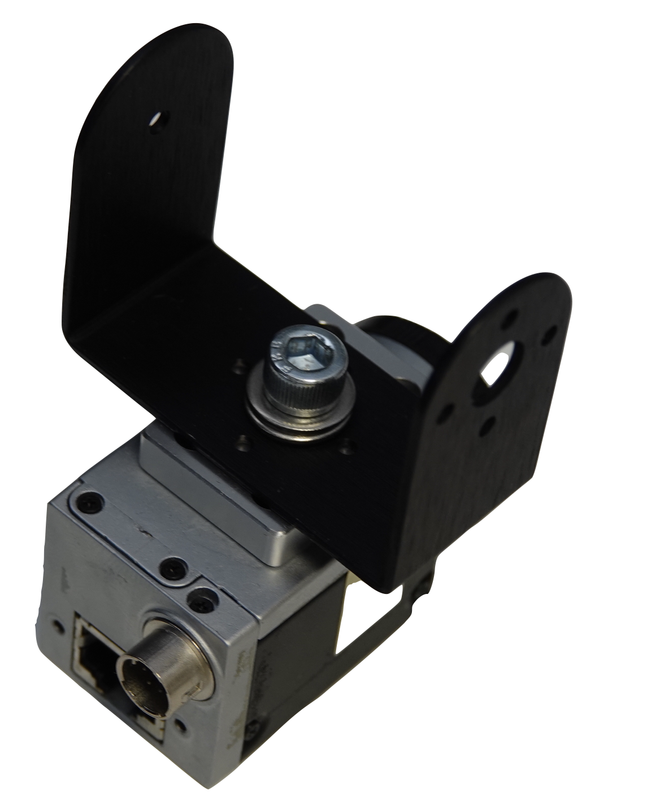
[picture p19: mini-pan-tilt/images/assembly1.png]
Assembly step 1


2. For each servo motor, replace the preinstalled "arm" with the disk shaped one:
   - turn the servo all the way counter-clockwise
   - remove arm
   - mount disk with '1' in the top position

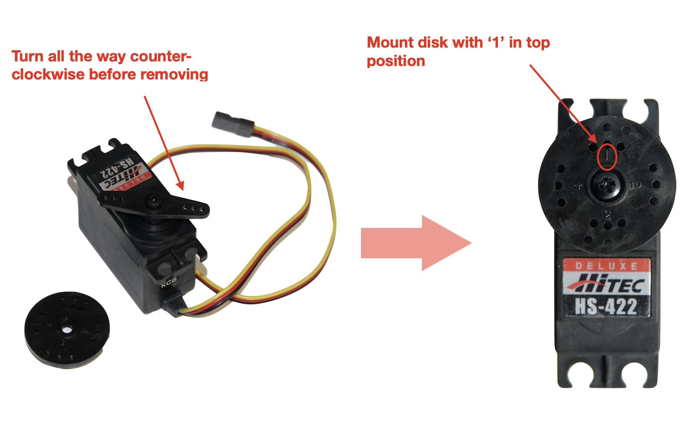
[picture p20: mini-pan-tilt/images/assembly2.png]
Assembly step 2.1


3. Mount multi-purpose servo bracket to pan-servo:
   - turn disk unitl '2' is in the top position
   - attach Multi-Puropse bracket in parallel with the servo. Use small balck screws to attach bracket to disk

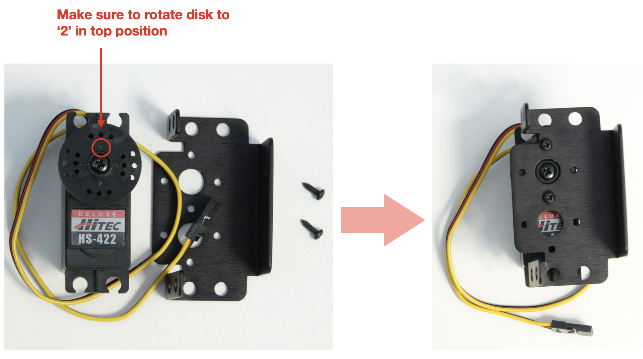
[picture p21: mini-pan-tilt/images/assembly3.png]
Assembly step 2.2


4. Mount tilt-servo:
   - attach one side of "C" bracket (with mounted camera) to the multi-purpose backet
   - mount tilt-servo to multi-purpose bracket using nylon rivets
   - **turn disk on tilt-servo to have '3' in top postition**
   - attach loose end of "C" bracket to disk. Make sure that the disk is in the right position!

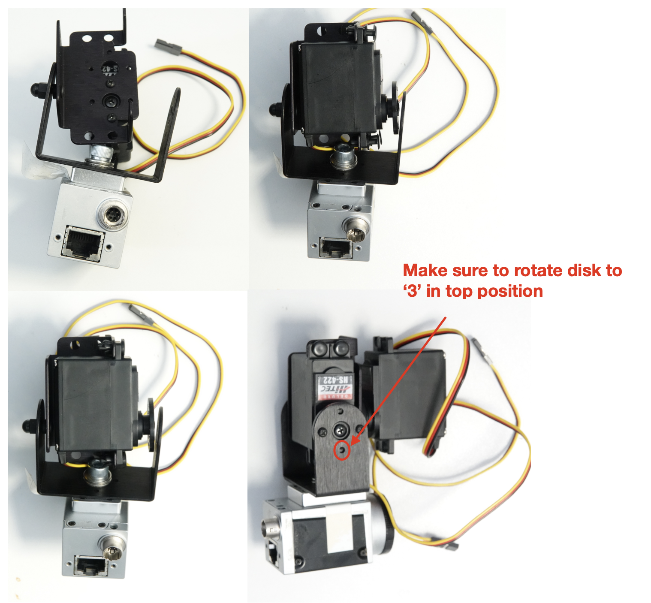
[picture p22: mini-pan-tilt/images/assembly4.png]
Assembly Step 2.3


5. Mount on base plate: - Attach 3D printed support bracket to base plate with M6 screw - attach pan-servo to support bracket using M3 x 20 screws and nuts

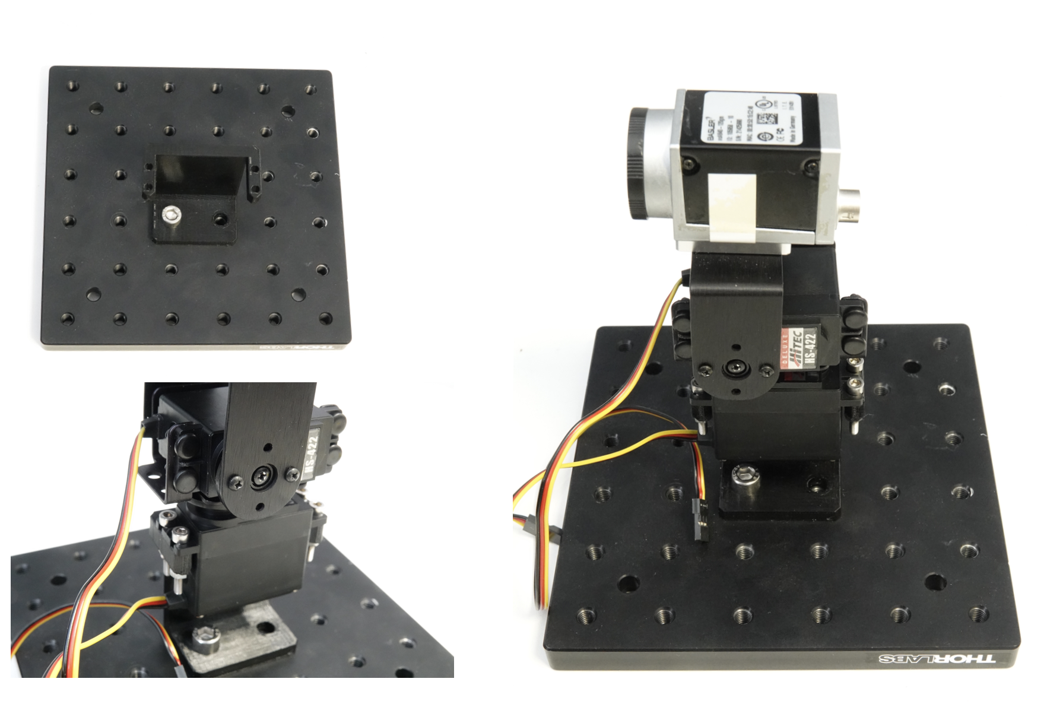
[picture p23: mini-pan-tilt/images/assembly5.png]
Assembly Step 2.4


6. Mount desired lens on camera

## Connecting the Raspberry Pi Pico

Each servo motor needs three connections to the microcontroller, representing

- black: GND
- red: VCC (Power)
- yellow: PWM, pulse (control)

These need to be soldered to the pins of the RPi Pico as follows

- gpio7 (PIN10): PWM tilt
- gpio6 (PIN9): PWM pan
- VBUS (PIN40): VCC of both servos
- arbitrary GND pins: GND of both servos

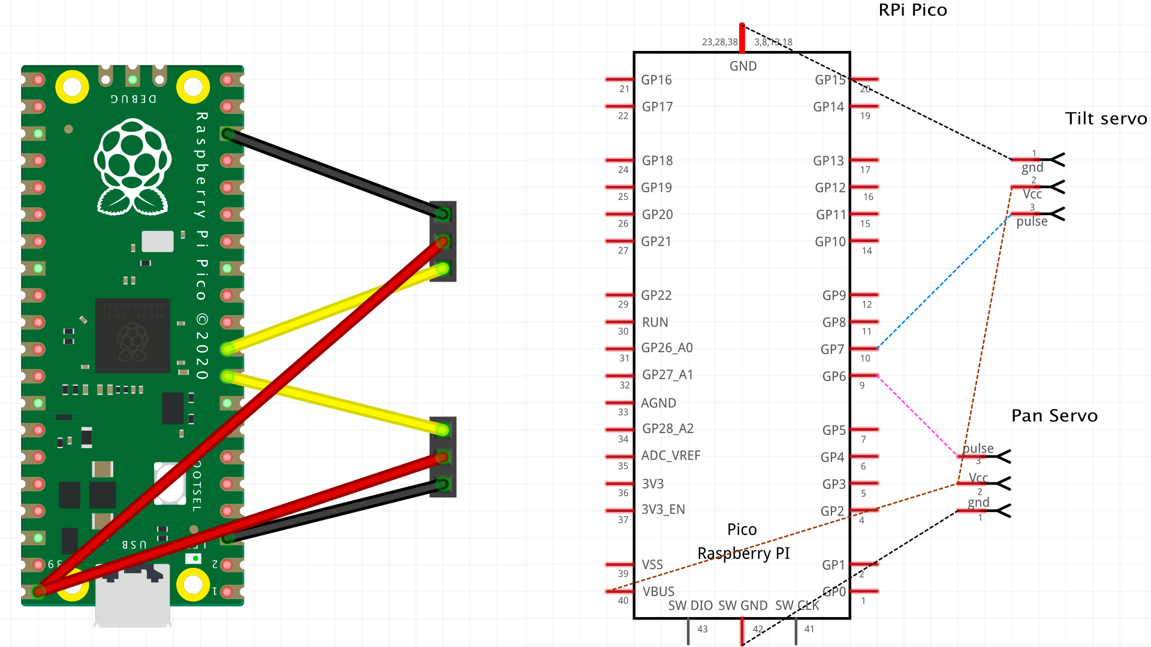
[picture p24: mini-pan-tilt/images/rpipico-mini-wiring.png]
rpipico wiring


either directly or via breadboard jumper cables (see below)

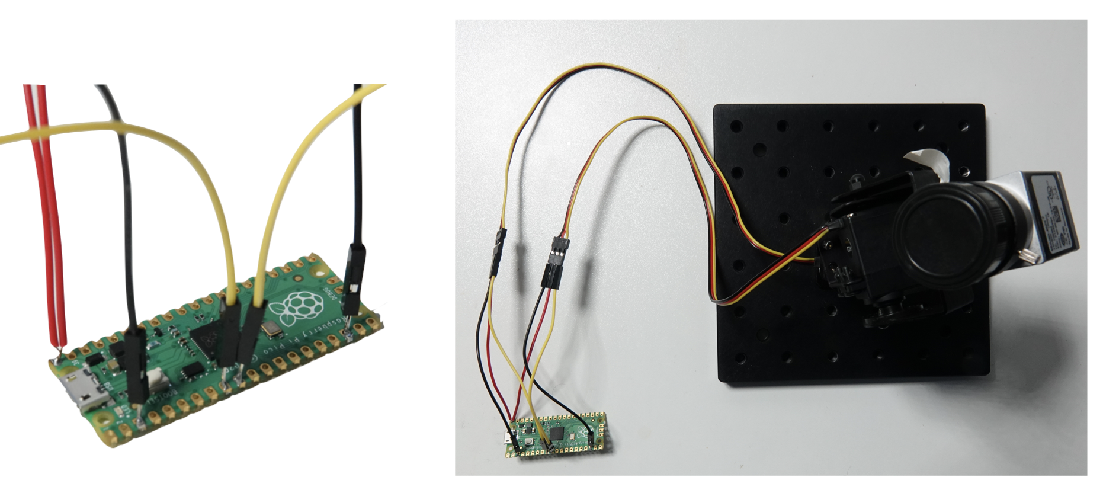
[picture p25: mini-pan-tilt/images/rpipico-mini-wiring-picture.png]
rpipico wiring picture


## Software & firmware installation

At present, the Beetrax system is based on two separate interacting software components operating in closed loop:

1. `strand-cam`: a multi- or single-camera visual tracking system, which provides positional information of the target to
2. `flo`: a fast-lock-on, closed-loop system controlling the movement of the camera(s) to keep them pointing toward the target

Both are written in `rust` and therefore require a working [rust installation](https://rustup.rs/) to build from source.

### 1. Install `strand-cam` via .deb package

> [!attention] Not tested yet!!

Install your camera drivers. Currently [Basler Pylon](<https://docs.baslerweb.com/software-installation-(linux)>) and Allied Vision Vimba are supported. It is highly recommended to use Basler components for this setup.

Connect the USB 3.0 camera to your machine and make sure that the `pylon Viewer` app recognizes the camera.

Now you can install strand-cam `version 0.12.0` or greater from https://github.com/strawlab/strand-braid.

`strand-cam` can now be opened globally by running

```sh
strand-cam-pylon
```

in the terminal. A new tab with the `strand-cam` browser-user-interface (BUI) will automatically open in your default browser.

### 2. Build `flo` from source

In a new terminal, clone the repository in to a location which will below be
called `/path/to/flo` and checkout `flo` as follows:

```bash
cd /path/to # <----change this to a suitable filesystem directory
git clone https://github.com/strawlab/flo
```

Install prerequisites for building the browser user interface (BUI):

- Install wasm-pack from here https://rustwasm.github.io/wasm-pack/installer/
- Install grass by running the following: `cargo install grass`

Next, we need to build the BUI:

```bash
cd /path/to/flo/crates/flo-bui
./build.sh
```

#### 2. Flashing firmware: PanTilt for RP-pico - Receive from USB (serial) and emit PWM for two servos

The following instructions how to flash rust firmware onto the RPi Pico is based on [rp2040-project-template](https://github.com/rp-rs/rp2040-project-template).

#### Installation of development dependencies

```sh
rustup target install thumbv6m-none-eabi
cargo install flip-link
cargo install elf2uf2-rs --locked
```

#### Running: We are going to load a UF2 over USB

First, navigate to `path/to/flo/firmware/rpipico-pantilt/`, which contains the firmware for the Raspberry Pi Pico.

_Step 1_ - Boot RP2040 into "USB Bootloader mode". Keep "BOOTSEL" button pressed while connecting to the PC. It should now be mounted in 'Flash drive' mode.

_Step 2_ - Use `cargo run`, which will compile the code and start the specified 'runner'. As the 'runner' is the `elf2uf2-rs` tool, it will build a UF2 file and copy it to your RP2040.

For a debug build:

```sh
cargo run
```

For a release build:

```bash
cargo run --release
```

### 3. configure `flo`

Navigate to `/path/to/flo`.

The `config-mini.yaml` file contains the specific configuration for the Mini-Pan-Tilt setup. Depending on your choice of camera and lens, you might need to modifiy the following lines:

```
centroid_to_sensor_x_angle_func:
# needs to be adjusted to specific camera/lens combitnation
  dx_gain: 0.00035 # 5.6 / 16mm (px pitch / focal length)
  dy_gain: 0.0
  offset: 0.0
centroid_to_sensor_y_angle_func:
  dx_gain: 0.0
  dy_gain: -0.00035 # same here, minus sign due to mounting
  offset: 0.0
```

### 4. run `flo` in open loop

Run flo with with the serial device and config file specified. Depending on your system, the path to the serial device might differ. In `/path/to/flo/pan-tilt-pc/` run

```bash
cargo run --release -- --pwm-serial /dev/serial/by-id/usb-Straw_Lab_Serial_port_TEST-if00 --config config-mini.yaml
```

The `flo` BUI is now available at several IP-addresses which are printed in the terminal window. You can open the BUI by `ctrl`- click on the IPs.

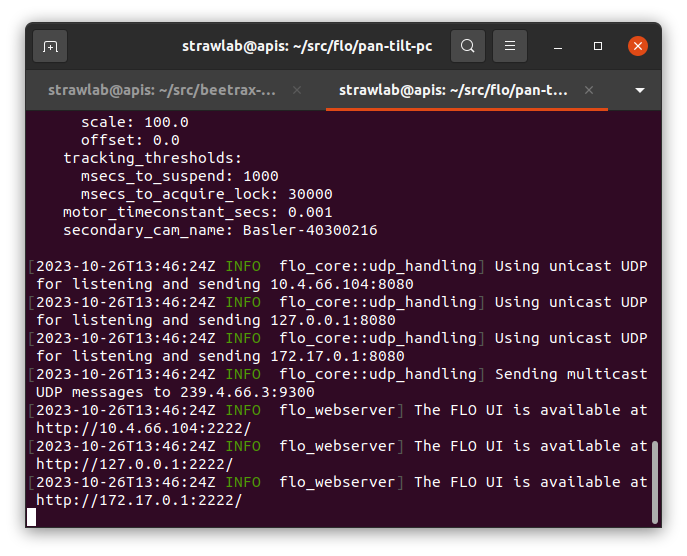
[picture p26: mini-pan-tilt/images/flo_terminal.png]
flo_terminal


The BUI will open up in a new browser tab in 'manual open loop' mode. Make sure the system behaves appropriately when setting new values for PAN and TILT of the home position. Unexpected behavior may occur if the motor positions during assembly were not as specified.

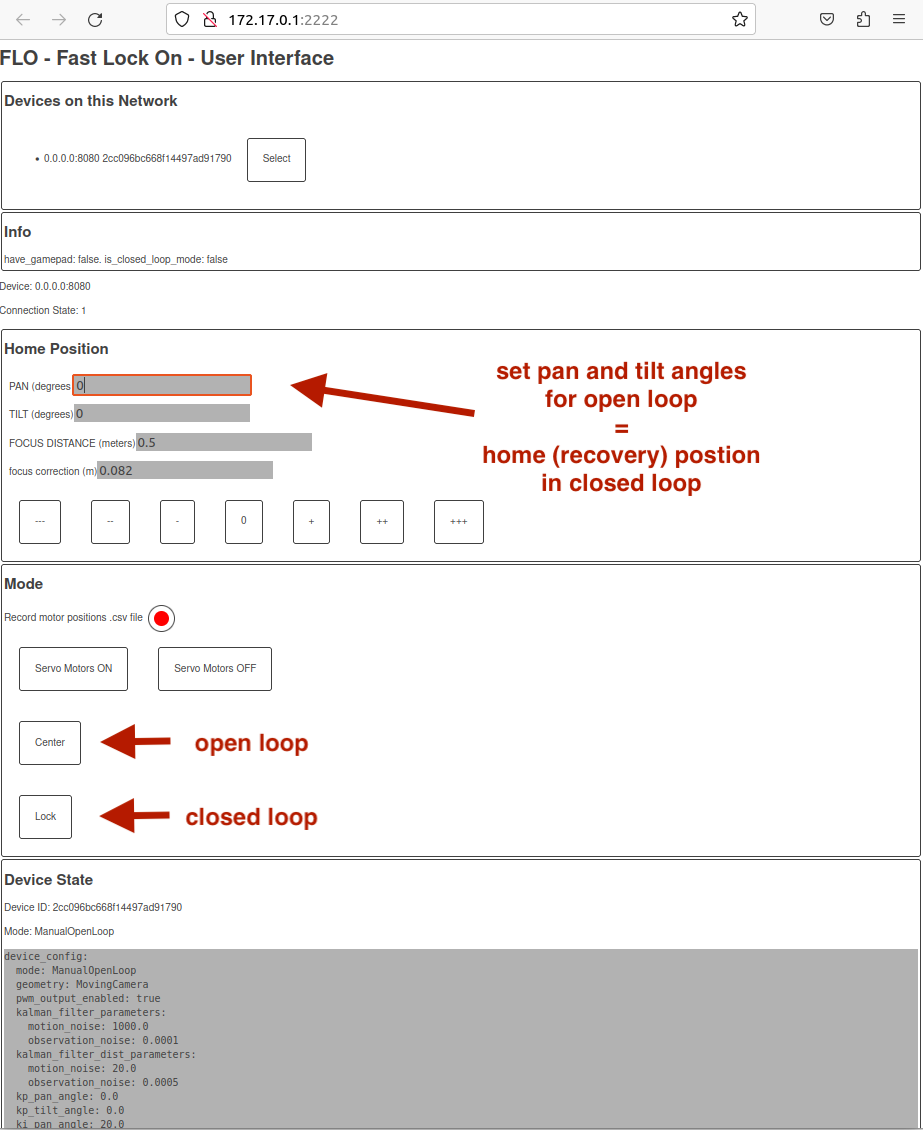
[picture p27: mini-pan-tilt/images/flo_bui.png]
flo_bui


### 5. configure `strand-cam`

If not already running, open `strand-cam` in a new terminal. The `strand-cam` BUI should open up in a new browser tab.

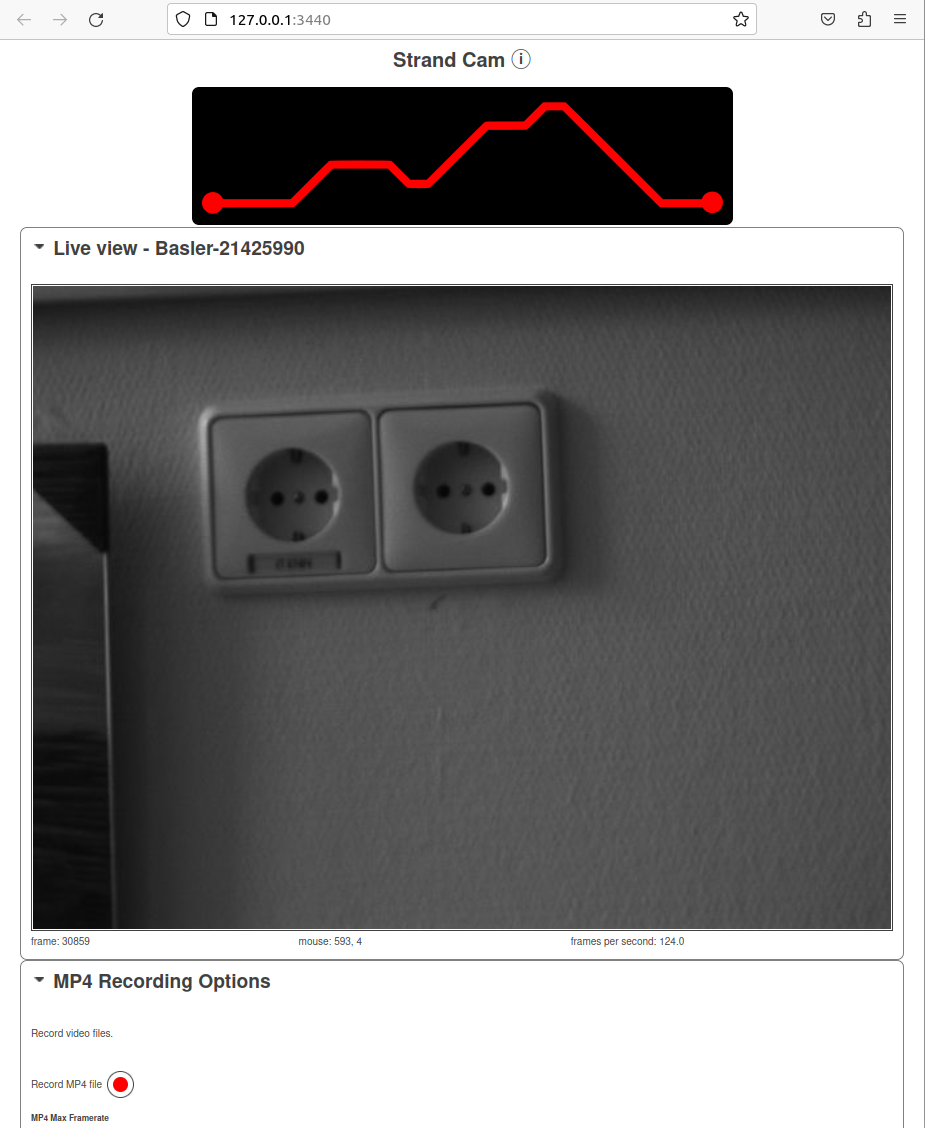
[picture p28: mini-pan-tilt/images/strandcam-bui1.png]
strandcam BUI1


Scroll down to the `Camera Settings' section and adjust exposure to improve signal-to-noise ratio, i.e. the tracked object (e.g. bright LED) should be visible and the background dark.

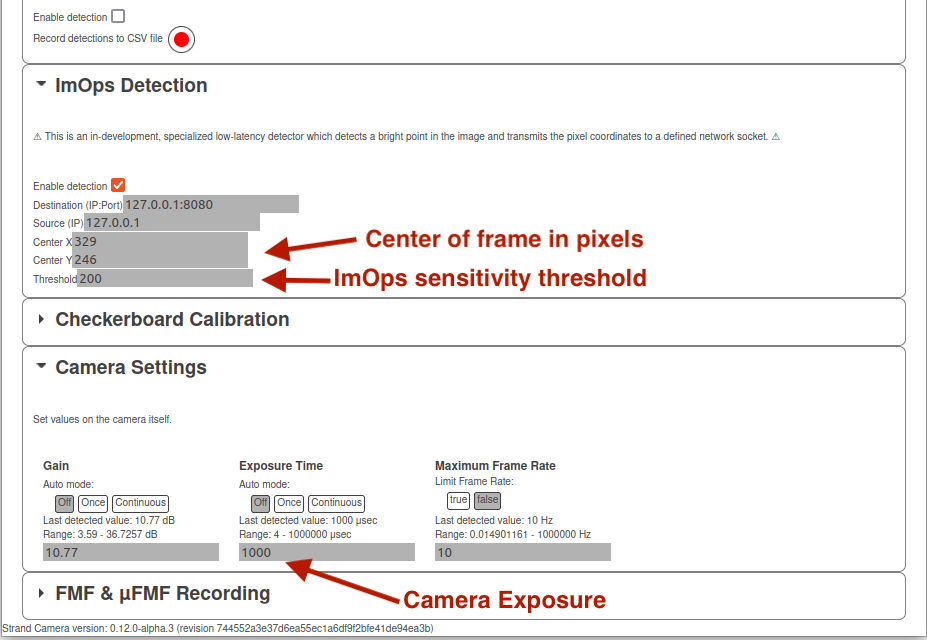
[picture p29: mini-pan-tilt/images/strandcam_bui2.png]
strandcam BUI2


Next, go to the 'ImOps Detection' section and enable it. Set the `Center X` and `Center Y` fields to the center of your image in pixels (can be determined from the 'Live view' section). Finally, set the sensitivity `Threshold` to 200.

In the 'Live view' window, there should now be a black circle which tracks the target. The ImOps data should now be broadcast to `flo`.

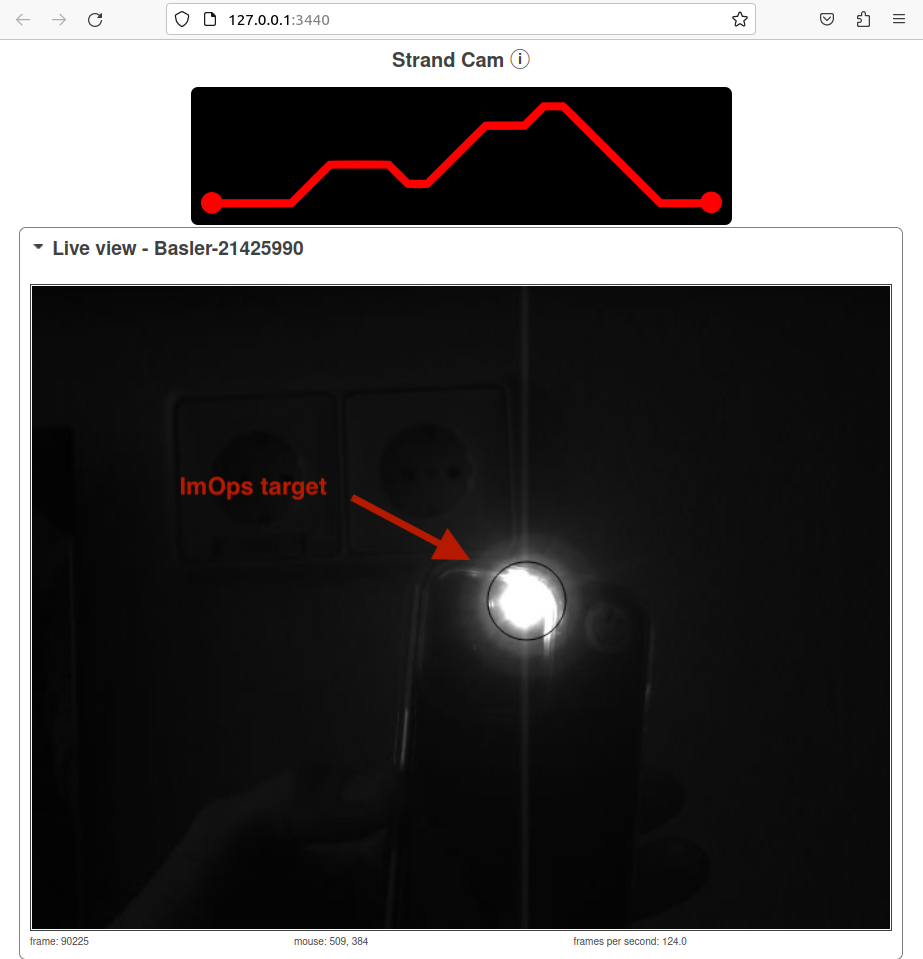
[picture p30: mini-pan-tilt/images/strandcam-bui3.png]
strandcam BUI3


### 6. run `flo` in closed loop mode

Go back the `flo` browser tab and click the `Lock` button. The camera should now lock on to the target when it enters the field of view.

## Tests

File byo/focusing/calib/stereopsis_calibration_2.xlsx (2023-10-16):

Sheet: Sheet1
real_distance | predicted_distance |  |  |  |  |  |  | main | stereo | offest
7 | 8.6 |  |  |  |  | T1 | x | 1169 | 1115 | 54
6 | 7.8 |  |  |  |  |  | y | 672 | 557 | 115
5 | 6.9
4 | 5.8 |  |  |  |  | T2 | x | 858 | 806 | 52
3 | 4.5 |  |  |  |  |  | y | 492 | 375 | 117
2 | 2.9
1 | 1.2 |  |  |  |  | empirical x_offset |  | 40
 |  |  |  |  |  | optical path up to front plate: 360mm
 |  |  |  | microsteps/2*pi rad focus motor | ms/rad focus motor
focus motor calibration |  |  |  | 508023
 |  |  |  | 524172
 | deg (estimated) | rad |  | 527726
barrel_angle_infty | 240 | 4.188790205
 | 1st
microsteps_min_focus | -42000 | 0
microsteps_infty_focus | -1640868
 | microstep/rad | small cog | large cog | microstep/rad motor
pan | 117437.6 | 17 | 245 | 8148.731429 | 31.83098214
tilt | 40764.3 | 20 | 100 | 8152.86 | 31.84710937
focus | 31742.10526 | 19 | 74 | 8150
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

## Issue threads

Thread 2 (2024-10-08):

### ISSUE TITLE
Missing link to 3D print file in mini-pan-tilt instructions

### ISSUE THREAD

**Issue by Seyij** [strawlab/flo-hardware#2]
Hello, thanks for the repo. In the instuctions here - https://github.com/strawlab/flo-hardware/blob/master/mini-pan-tilt/mini-pan-tilt-build-instructions.md at line 23. It doesn't include the link to the "custom 3D printed support bracket". It doesn't list the name of the file so I was unable to locate it.

**Comment by astraw** [comment]
Oh, we had forgotten to upload that particular file (and another one). We now updated the repo in 85364564bdc6918a3db84ef1b8dc5a44d9d6a73c and b97a988d5e35905346d01b98ac3c5f17215afbbb. Thanks for the note!

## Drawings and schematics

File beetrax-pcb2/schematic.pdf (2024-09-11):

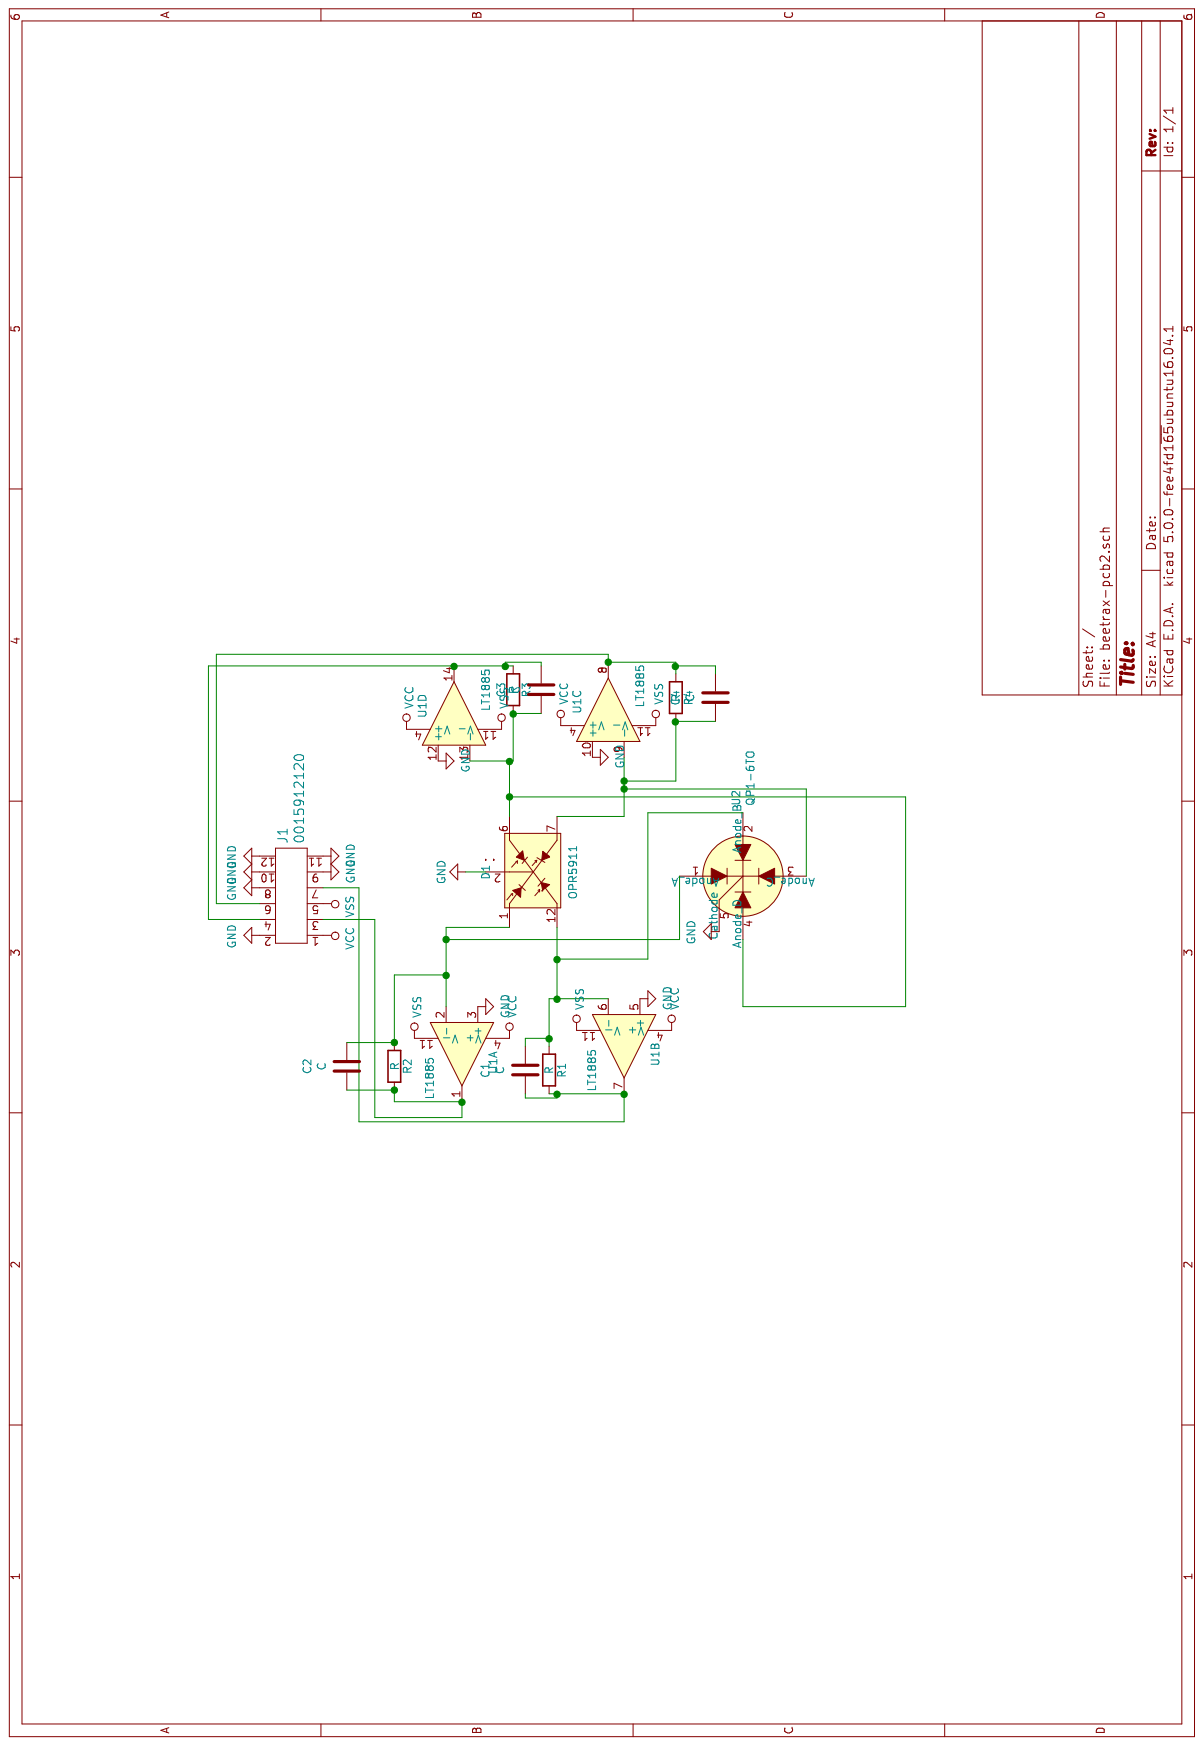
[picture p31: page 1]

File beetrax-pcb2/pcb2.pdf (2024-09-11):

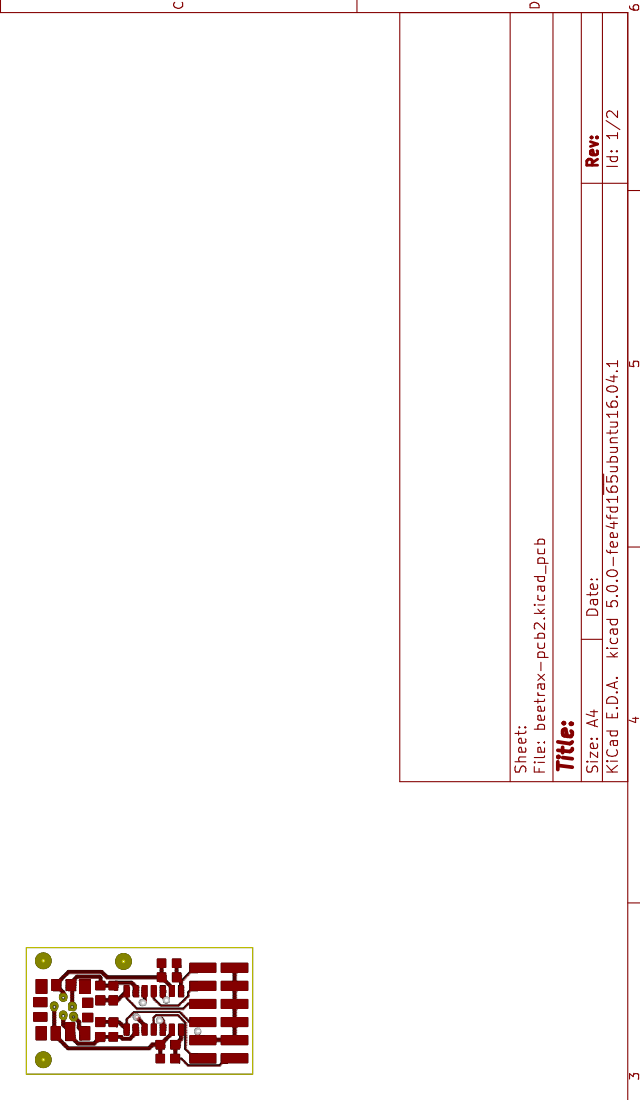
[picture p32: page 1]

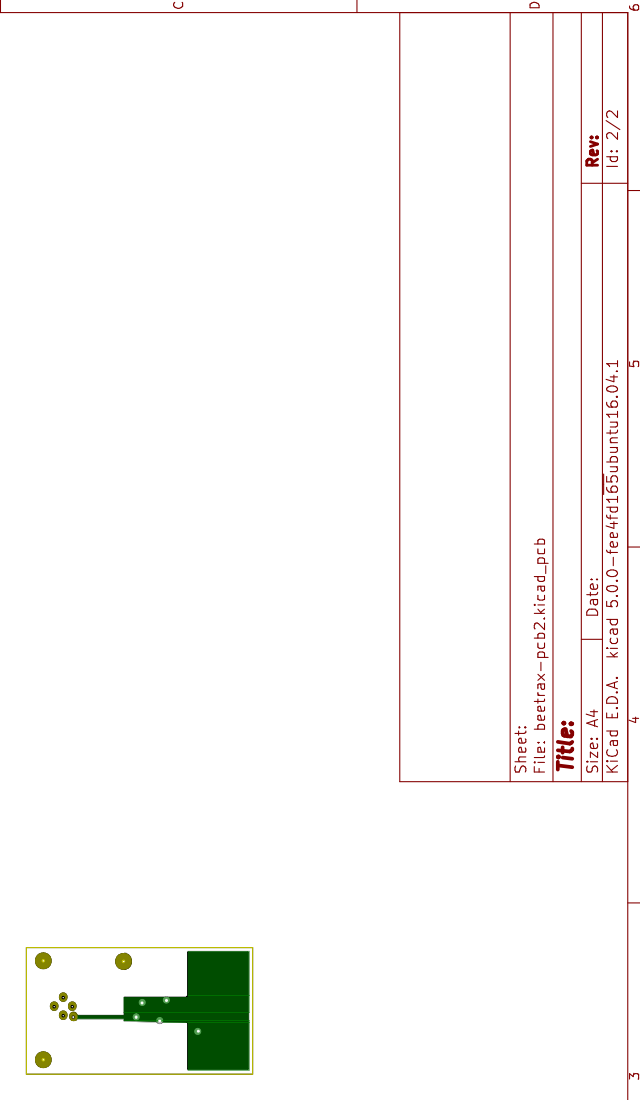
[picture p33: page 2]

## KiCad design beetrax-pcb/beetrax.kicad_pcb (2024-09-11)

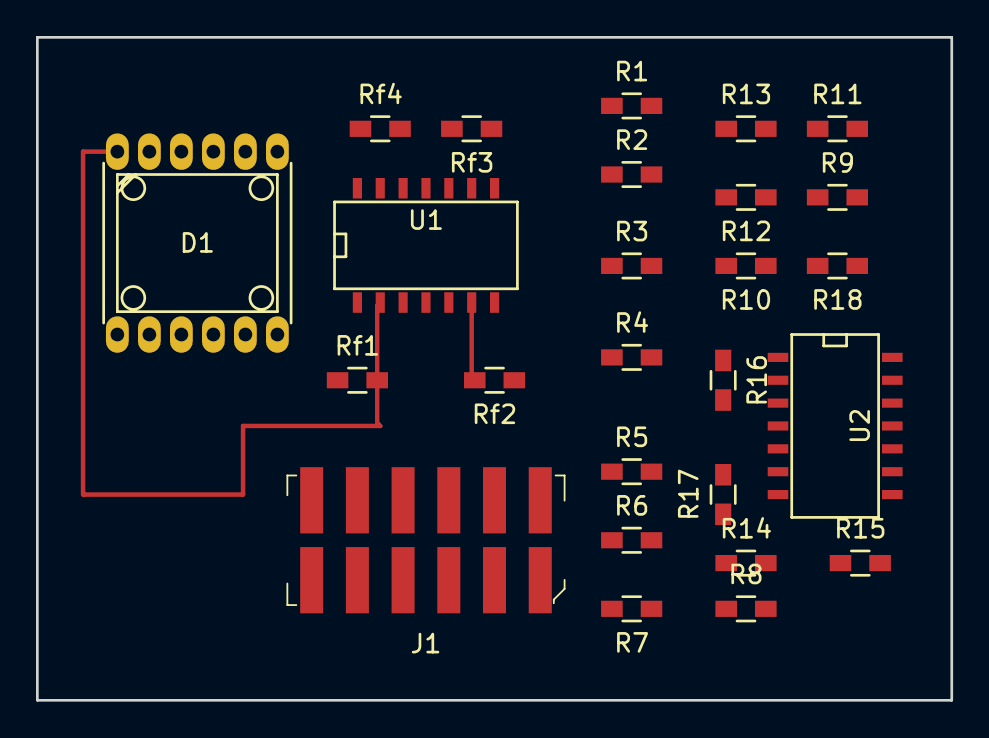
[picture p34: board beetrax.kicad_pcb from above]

Board: 2 copper layers, 50.8 x 36.8 mm, 26 parts (0 on the bottom side), 22 nets.

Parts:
D1: OPR5911; eDIP-12
J1: 0015912120; PinHeader_2x6_P2.54mm_Vertical_SMD
R1, R2, R3, R4, R5, R6, R7, R8, R9, R10, R11, R12, R13, R14, R15, R16, R17, R18: R; R_0603_HandSoldering
Rf1, Rf2, Rf3, Rf4: R; R_0603_HandSoldering
U1, U2: LT1885; SOIC-14_N

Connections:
GND: J1.5, R13.1, R14.1, R15.1, U1.3, U1.10
unnamed: D1.1, Rf1.1, U1.2
unnamed: D1.6, Rf2.2, U1.6
unnamed: D1.7, Rf3.2, U1.9
unnamed: D1.12, Rf4.1, U1.13
unnamed: J1.1, R3.2, R8.2, R9.2, Rf1.2, U1.1
unnamed: J1.2, R16.1, Rf4.2, U1.14, U2.1
unnamed: R4.2, R5.2, R10.2
unnamed: J1.4, R17.1, U2.7
unnamed: R1.2, R6.2, R11.2
unnamed: J1.6, R18.1, U2.8
unnamed: R2.2, R7.2, R12.2
unnamed: J1.11, Rf2.1, U1.7
unnamed: J1.12, Rf3.1, U1.8
unnamed: R1.1, R2.1, R13.2, U2.3
unnamed: R9.1, R10.1, R11.1, R12.1, R18.2, U2.9
unnamed: R5.1, R6.1, R14.2, U2.5
unnamed: R15.2, U2.10
unnamed: R3.1, R4.1, R16.2, U2.2
unnamed: R7.1, R8.1, R17.2, U2.6
VCC: J1.7, U1.4, U2.4
VSS: J1.3, U1.11, U2.11

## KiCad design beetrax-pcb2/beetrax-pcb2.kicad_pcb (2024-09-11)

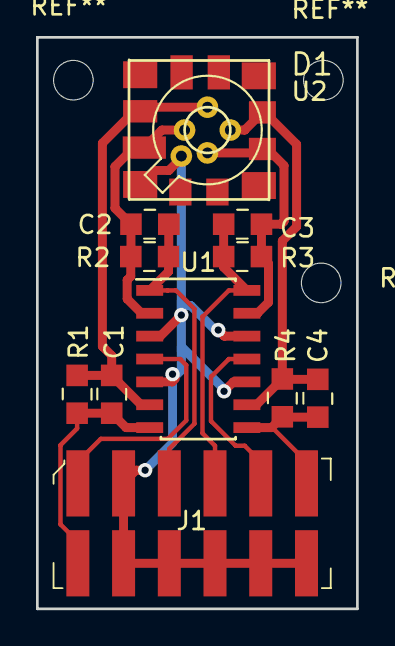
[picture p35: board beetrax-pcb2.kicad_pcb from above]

Board: 2 copper layers, 17.8 x 31.8 mm, 12 parts (0 on the bottom side), 11 nets.

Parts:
C1, C2, C3, C4: C; 0805
D1: OPR5911
J1: 0015912120; PinHeader_2x6_P2.54mm_Vertical_SMD
R1, R2, R3, R4: R; 0805
U1: LT1885; SOIC-14_3.9x8.7mm_P1.27mm
U2: QP1-6TO; QP1-6TOv2

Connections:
GND: D1.2, J1.2, J1.8, J1.9, J1.10, J1.11, J1.12, U1.3, U1.5, U1.10, U1.12, U2.5
unnamed: C1.1, D1.12, R1.1, U1.6, U2.2
unnamed: C1.2, J1.7, R1.2, U1.7
unnamed: C2.1, D1.1, R2.1, U1.2, U2.1
unnamed: C2.2, J1.3, R2.2, U1.1
unnamed: C3.1, J1.4, R3.1, U1.14
unnamed: C3.2, D1.6, R3.2, U1.13, U2.4
unnamed: C4.1, J1.6, R4.1, U1.8
unnamed: C4.2, D1.7, R4.2, U1.9, U2.3
VCC: J1.1, U1.4
VSS: J1.5, U1.11

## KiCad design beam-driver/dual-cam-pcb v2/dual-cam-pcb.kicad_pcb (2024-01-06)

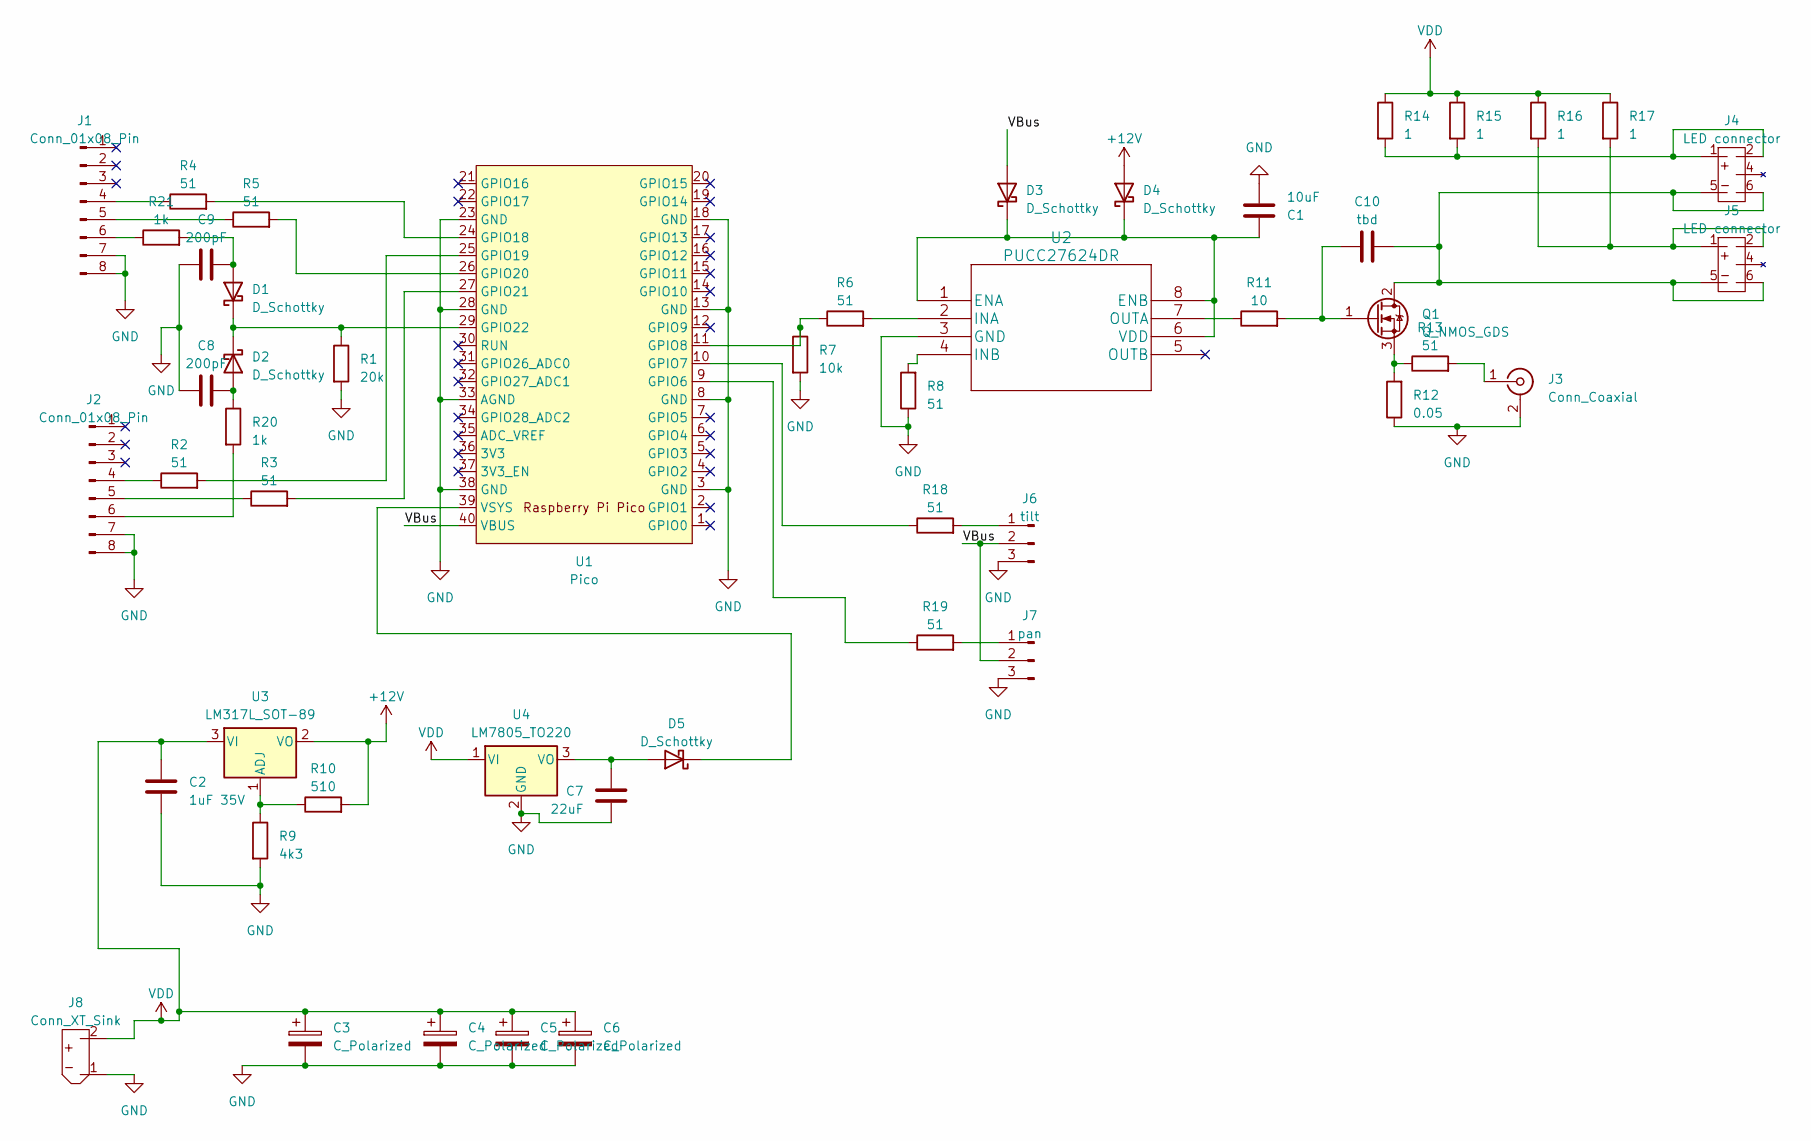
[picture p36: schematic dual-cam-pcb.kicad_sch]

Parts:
C1: 10uF; C_0805_2012Metric_Pad1.18x1.45mm_HandSolder
C2: 1uF 35V; C_0805_2012Metric_Pad1.18x1.45mm_HandSolder
C3: C_Polarized; CP_Radial_D18.0mm_P7.50mm
C4, C5, C6: C_Polarized
C7: 22uF; C_1206_3216Metric_Pad1.33x1.80mm_HandSolder
C8, C9: 200pF; C_0603_1608Metric_Pad1.08x0.95mm_HandSolder
C10: tbd; C_0603_1608Metric_Pad1.08x0.95mm_HandSolder
D1, D2: D_Schottky; D_MicroMELF_Handsoldering
D3, D4, D5: D_Schottky; D_0805_2012Metric_Pad1.15x1.40mm_HandSolder
J1, J2: Conn_01x08_Pin; PinHeader_1x08_P2.54mm_Vertical
J3: Conn_Coaxial; SMA_Amphenol_901-144_Vertical
J4, J5: LED connector; Conn_LED_source
J6: tilt; PinHeader_1x03_P2.54mm_Vertical
J7: pan; PinHeader_1x03_P2.54mm_Vertical
J8: Conn_XT_Sink; AMASS_XT30U-M_1x02_P5.0mm_Vertical
Q1: Q_NMOS_GDS; TO-252-2
R1: 20k; R_0603_1608Metric_Pad0.98x0.95mm_HandSolder
R2, R3, R4, R5, R6, R8, R13, R18, R19: 51; R_0603_1608Metric_Pad0.98x0.95mm_HandSolder
R7: 10k; R_0603_1608Metric_Pad0.98x0.95mm_HandSolder
R9: 4k3; R_0603_1608Metric_Pad0.98x0.95mm_HandSolder
R10: 510; R_0603_1608Metric_Pad0.98x0.95mm_HandSolder
R11: 10; R_0603_1608Metric_Pad0.98x0.95mm_HandSolder
R12: 0.05; R_2010_5025Metric_Pad1.40x2.65mm_HandSolder
R14, R15, R16, R17: 1; R_Axial_DIN0411_L9.9mm_D3.6mm_P5.08mm_Vertical
R20, R21: 1k; R_0603_1608Metric_Pad0.98x0.95mm_HandSolder
U1: Pico; RPi_Pico_SMD
U2: PUCC27624DR; SOIC-8_3.9x4.9mm_P1.27mm
U3: LM317L_SOT-89; SOT-89-3
U4: LM7805_TO220; TO-220-3_Vertical

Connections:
+12V: D4.2 (A), R10.2, U3.2 (VO)
/VBus: D3.2 (A), J6.2, J7.2, U1.40 (VBUS)
GND: C1.2, C2.2, C3.2, C4.2, C5.2, C6.2, C7.1, C8.2, C9.2, J1.7, J1.8, J2.7, J2.8, J3.2 (Ext), J6.3, J7.3, J8.1 (minus1), R1.2, R7.2, R8.1, R9.2, R12.1, U1.3 (GND), U1.8 (GND), U1.13 (GND), U1.18 (GND), U1.23 (GND), U1.28 (GND), U1.33 (AGND), U1.38 (GND), U2.3 (GND), U4.2 (GND)
unnamed: C9.1, D1.2 (A), R21.2
unnamed: D1.1 (K), D2.1 (K), R1.1, U1.29 (GPIO22)
unnamed: C8.1, D2.2 (A), R20.1
unnamed: C1.1, D3.1 (K), D4.1 (K), U2.1 (ENA), U2.6 (VDD), U2.8 (ENB)
unnamed: C7.2, D5.2 (A), U4.3 (VO)
unnamed: D5.1 (K), U1.39 (VSYS)
unnamed: J1.4, R4.1
unnamed: J1.5, R5.1
unnamed: J1.6, R21.1
unnamed: J2.4, R2.1
unnamed: J2.5, R3.1
unnamed: J2.6, R20.2
unnamed: J3.1 (In), R13.2
unnamed: C10.1, J4.5 (minus1), J4.6 (minus2), J5.5 (minus1), J5.6 (minus2), Q1.2 (D)
unnamed: J4.1 (plus1), J4.2 (plus2), R14.2, R15.2
unnamed: J5.1 (plus1), J5.2 (plus2), R16.2, R17.2
unnamed: J6.1, R18.2
unnamed: J7.1, R19.2
unnamed: C10.2, Q1.1 (G), R11.2
unnamed: Q1.3 (S), R12.2, R13.1
unnamed: R19.1, U1.9 (GPIO6)
unnamed: R18.1, U1.10 (GPIO7)
unnamed: R6.1, R7.1, U1.11 (GPIO8)
unnamed: R4.2, U1.24 (GPIO18)
unnamed: R2.2, U1.25 (GPIO19)
unnamed: R5.2, U1.26 (GPIO20)
unnamed: R3.2, U1.27 (GPIO21)
unnamed: R6.2, U2.2 (INA)
unnamed: R8.2, U2.4 (INB)
unnamed: R11.1, U2.7 (OUTA)
unnamed: R9.1, R10.1, U3.1 (ADJ)
VDD: C2.1, C3.1, C4.1, C5.1, C6.1, J8.2 (plus), R14.1, R15.1, R16.1, R17.1, U3.3 (VI), U4.1 (VI)

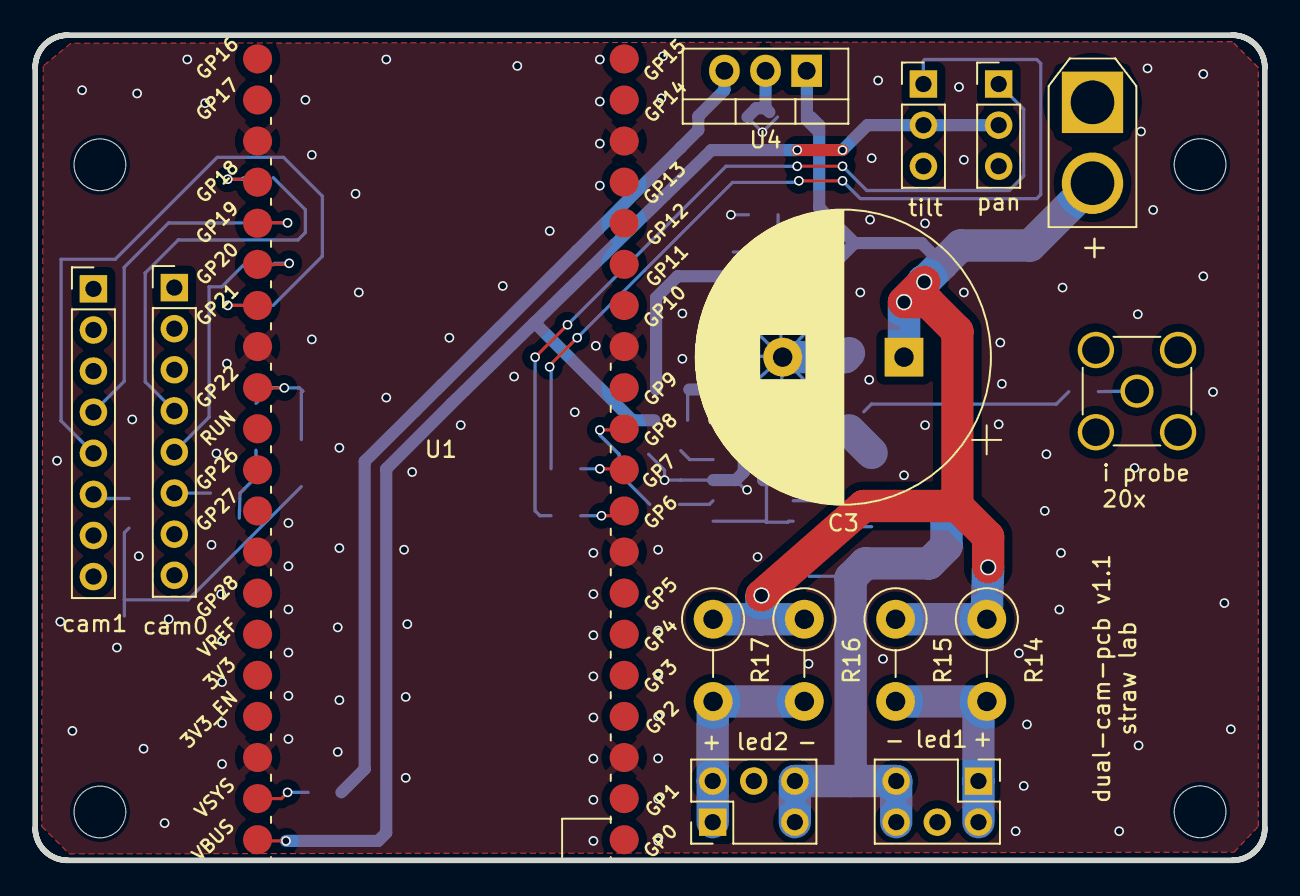
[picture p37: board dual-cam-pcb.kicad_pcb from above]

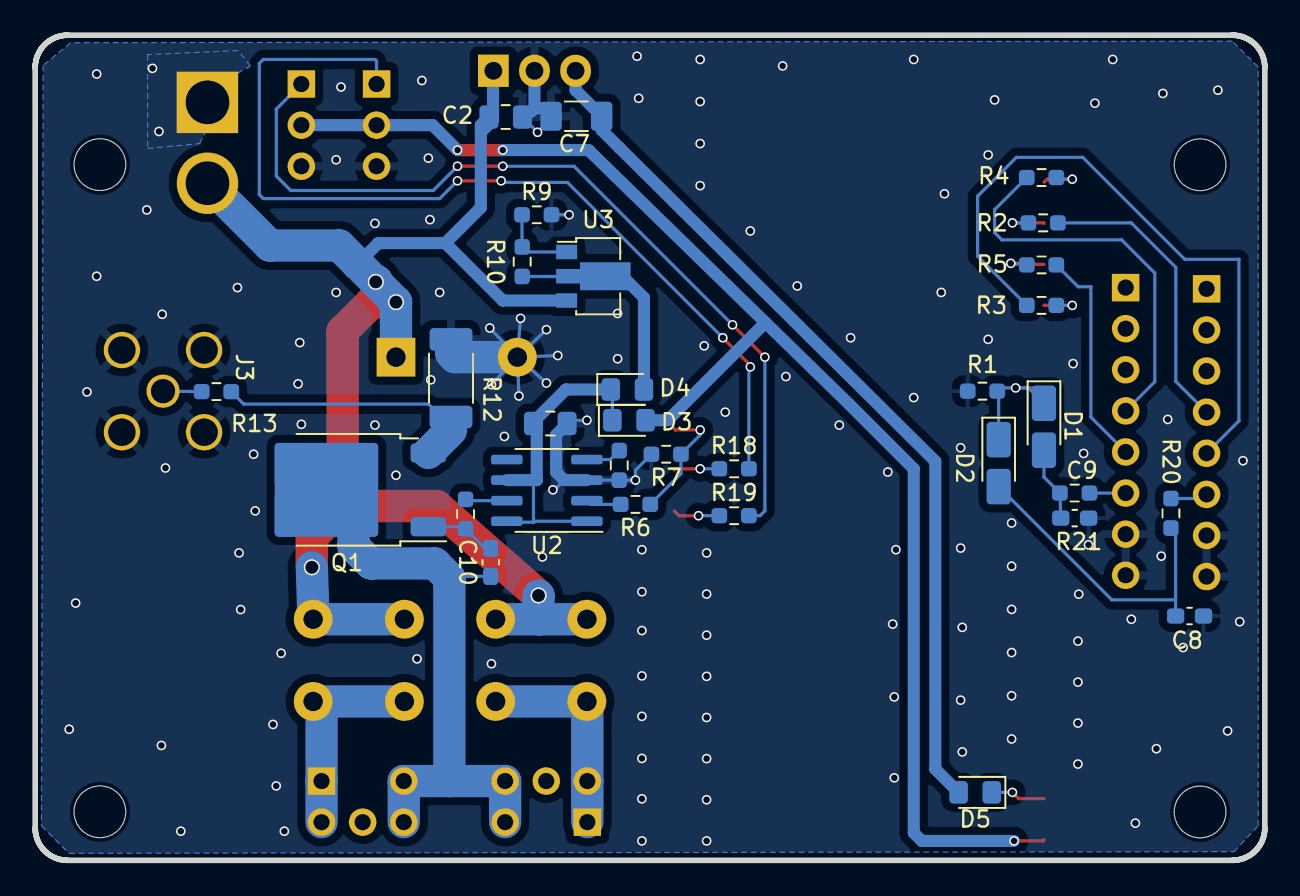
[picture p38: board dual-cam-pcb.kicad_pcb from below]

Board: 2 copper layers, 76.0 x 51.0 mm, 46 parts (31 on the bottom side), 35 nets.

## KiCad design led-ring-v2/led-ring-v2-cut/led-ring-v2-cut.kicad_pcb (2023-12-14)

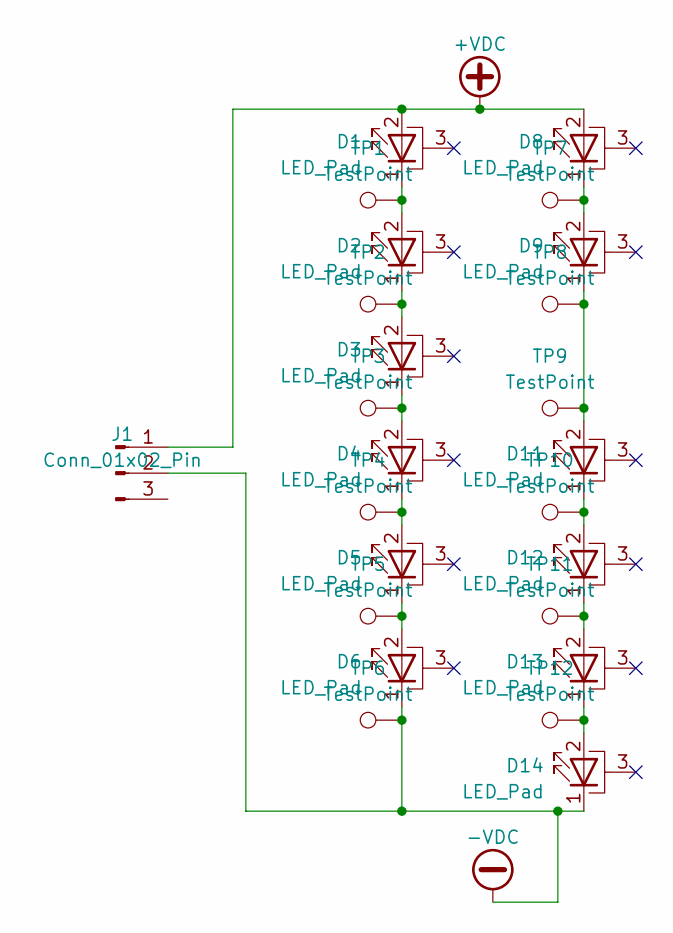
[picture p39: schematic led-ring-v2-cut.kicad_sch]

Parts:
D1, D2, D3, D4, D5, D6, D8, D9, D11, D12, D13, D14: LED_Pad; OSRAM_SFH_4715AS_with_LISA4
J1: Conn_01x02_Pin; strawlab_led_conn_M_smd
TP1, TP2, TP3, TP4, TP5, TP6, TP7, TP8, TP9, TP10, TP11, TP12: TestPoint; TestPoint_Pad_D1.0mm_paste

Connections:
+VDC: D1.2 (A), D8.2 (A), J1.1
-VDC: D6.1 (K), D14.1 (K), J1.2, TP6.1
unnamed: D1.1 (K), D2.2 (A), TP1.1
unnamed: D2.1 (K), D3.2 (A), TP2.1
unnamed: D3.1 (K), D4.2 (A), TP3.1
unnamed: D4.1 (K), D5.2 (A), TP4.1
unnamed: D5.1 (K), D6.2 (A), TP5.1
unnamed: D8.1 (K), D9.2 (A), TP7.1
unnamed: D9.1 (K), D11.2 (A), TP8.1, TP9.1
unnamed: D11.1 (K), D12.2 (A), TP10.1
unnamed: D12.1 (K), D13.2 (A), TP11.1
unnamed: D13.1 (K), D14.2 (A), TP12.1

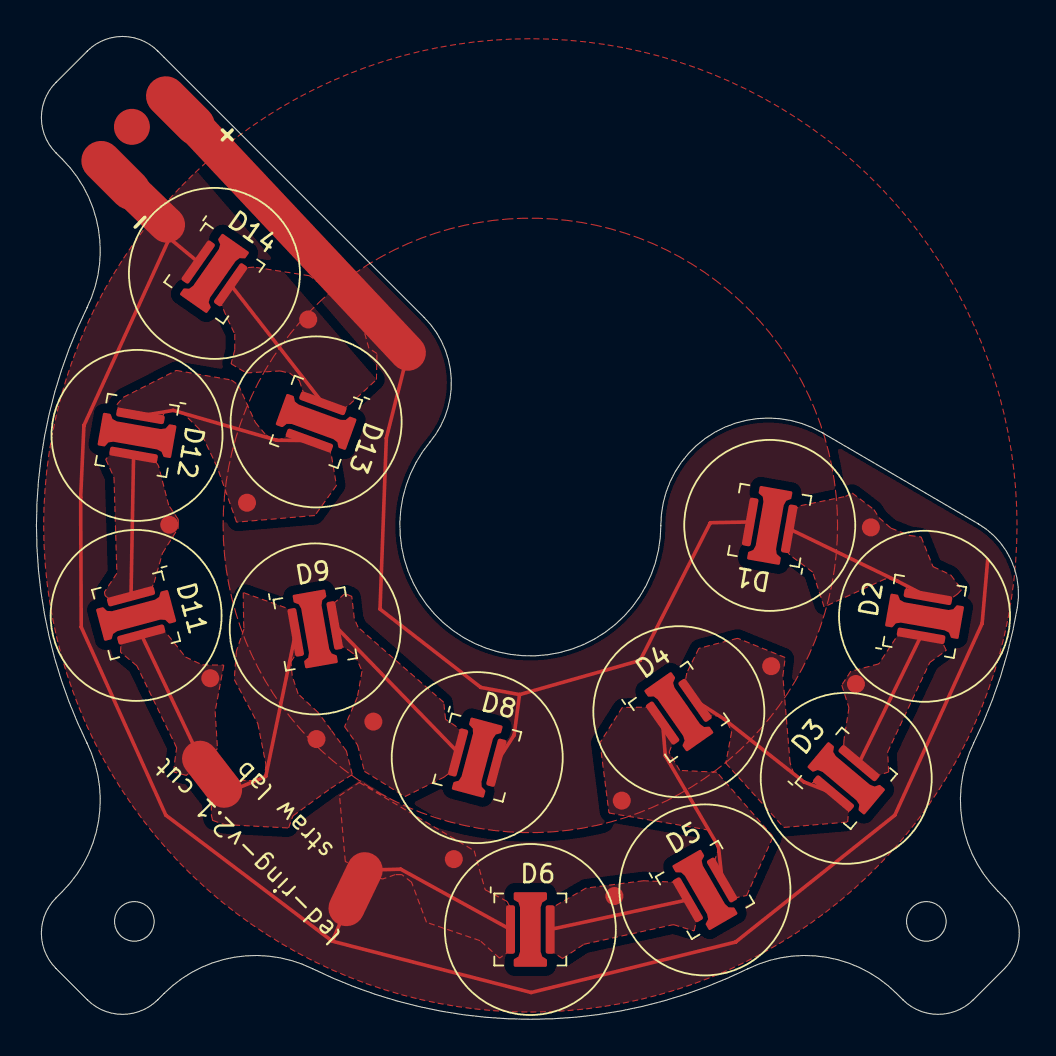
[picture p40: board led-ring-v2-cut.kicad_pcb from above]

Board: 2 copper layers, 54.6 x 54.6 mm, 25 parts (0 on the bottom side), 12 nets.

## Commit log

2023-10-16 add bom, pcbs, some 3d prints
    [10mm lens packing-Compound.dxf, 10mm lens packing-board outline.dxf, 10mm lens packing-fill zones (Sketch004).dxf, 10mm lens packing.FCStd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]
2023-10-17 update beam-driver pcb
    to include emi filter on ExposureActive camera GPIO.
    + update gerbers
    [dual-cam-pcb-B_Cu.gbr, dual-cam-pcb-B_Mask.gbr, dual-cam-pcb-B_Silkscreen.gbr, dual-cam-pcb-Edge_Cuts.gbr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]
2023-10-17 Add led driver components to bom
    + a few other minor changes to bom
    [bom.xlsx, dual-cam-pcb-bom.xlsx]
2023-10-18 add step files for focusing parts
    [36jx30k5.18-mount.step, 36jx30k5.18-pinion.step]
2023-10-23 move byo stuff into `byo` folder
    in anticipation of adding other flo hardware here
    [2cam-plate-35mm.FCStd, 2cam-plate-35mm.stl, 36jx30k5.18-mount.FCStd, 36jx30k5.18-mount.step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]
2023-10-23 document trigger cable
2023-10-28 fix belt profile name
    [bom.xlsx]
2023-10-29 add 3d print parts
    [bom.xlsx]
2023-12-14 led-ring-v2.1
    * fix polarity markings
    * add lens circles to aid glue deposition
    [led-ring-v2-Edge_Cuts.gbr, led-ring-v2-F_Cu.gbr, led-ring-v2-F_Mask.gbr, led-ring-v2-F_Paste.gbr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]
2023-12-14 create cut version of led ring
    [10mm lens packing (cut version)-board outline.dxf, 10mm lens packing (cut version).FCStd, led-ring-v2-cut.kicad_pcb, led-ring-v2-cut.kicad_sch]
2023-12-14 led-ring-v2-cut: fab files
    [led-ring-v2-cut-Edge_Cuts.gbr, led-ring-v2-cut-F_Cu.gbr, led-ring-v2-cut-F_Mask.gbr, led-ring-v2-cut-F_Silkscreen.gbr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]
2023-12-15 mention cut pcb in instructions
2023-12-15 update dual-cam-pcb
    * change some footprints
    * add miller capacitor (to smooth out led transitions)
    * add pcb name
    * minor layout changes
    [dual-cam-pcb.kicad_pcb, dual-cam-pcb.kicad_sch]
2023-12-15 delete outdated gerbers
    fab services accept kicadpcbs directly, usually
    [dual-cam-pcb-B_Cu.gbr, dual-cam-pcb-B_Mask.gbr, dual-cam-pcb-B_Silkscreen.gbr, dual-cam-pcb-Edge_Cuts.gbr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]
2024-01-02 update BYO BOM
    * fix "system" field for pantilt components
    * update led-ring references to cut version
    * add power supplies
    * add usb cables for motors
    * add some part numbers for dual-cam-pcb
    * other changes
    [bom.xlsx]
2024-01-03 add bugs.txt for dual-cam-pcb
2024-01-06 dual-cam-pcb: update cheatsheet layer
    [dual-cam-pcb.kicad_pcb]
2024-02-09 bom: refine ball head
    [bom.xlsx]
2024-03-07 Increase thickness of pan cover to 2 mm.
    Some printers can not print the previous version.
    [Pan_cover_2mm.stl]
2024-09-11 import PCB designs
    from internal `flo` repo commit
    726013358700dc3df1ec6a66a7fca4f67ebcc50a
    [beetrax-pcb2-2018-08-01-13-12-05.sch, beetrax-pcb2-B.Cu.gbr, beetrax-pcb2-B.Mask.gbr, beetrax-pcb2-B.Paste.gbr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]
2024-10-08 add mini-pan-tile STL files
    [a2A1920_adapter_6mm.stl, motor_holder.stl]
